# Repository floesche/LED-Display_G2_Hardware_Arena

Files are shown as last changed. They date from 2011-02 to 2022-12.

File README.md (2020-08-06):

---
title: Arena PCBs
parent: Generation 2
---

## Project content

```
├── arena_12_20
│   ├── gerber_v1
│   ├── gerber_v2
│   ├── pdf
│   └── svg
├── arena_12_20_top
│   └── gerber_v1
├── arena_mini
│   ├── gerber_v1
│   └── pdf
├── full
│   ├── 12-ring
│   └── 24-ring
├── mod
├── pdfs
├── planar_arena_8x
│   └── gerber_v0p1
└── planar_arena_8x_base
    ├── v0p1
    └── v0p2
```

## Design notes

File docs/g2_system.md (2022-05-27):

---
title: Generation 2
has_children: true
has_toc: false
nav_order: 20
permalink: /G2/
---

# Panels System

For a long time and since [Michael Reiser](https://www.janelia.org/people/michael-reiser) started an online documentation of the Modular LED Displays more than a decade ago, this introductory text had emphasized the community aspect of this endeavor. It is no small feat to design and produce electrical systems with high temporal and spatial precision that work reliably in many different scientific settings. Many labs have taken this task upon themselves and are building and using these systems. By now, the [Generation 2](g2_system.md) and [3]({{site.baseurl}}/G3/) Modular LED Displays have a large user basis across many scientific labs. We are also confident that the additional capabilities of the [Generation 4]({{site.baseurl}}/G4/) system will further the spread of this new stimulus presentation systems, especially once we had the chance to explain the advantages in the upcoming methods paper. Through all this, the exchange of experiences coupled with suggestions and improvements has benefited the system. Please [keep sending]({{site.baseurl}}/Contact) updates, improvements, and troubleshooting suggestions -- this is invaluable support for us in making the current and future systems better, but also for any future scientist who wants to replicate one of the systems in their setup.

To get started with [Generation 2](g2_system.md) or even a [Generation 3]({{site.baseurl}}/G3/) system, please have a look at this current page where we show some technical details of the system. A more general [user guide](g2_user-guide.md), written by Mark Frye, Michael Dickinson, and Michael Reiser, gives a nice and informal introduction to this system and its use as a flight arena for flies. Finally, we still consider the dated but [timeless paper](https://doi.org/10.1016/j.jneumeth.2007.07.019) that introduced the Modular LED Display back in 2007 a useful reference.

__Note__: For historical reasons we provide some information on how to [install](g2_prerequisites.md) a Generation 2 system, although we would strongly discourage anyone from doing this at this point. Follow the documentation of [Generation 4]({{site.baseurl}}/G4/) system instead or, if you want to use a less expensive system, have a look at the [Generation 3]({{site.baseurl}}/G3/) Modular LED Display instead.
{:.info}

# System Overview

The system has been designed to allow for rapid development of behavioral (visual) stimuli. There are three components to the system:

- __The displays__: These are 8×8 dot matrix displays of LEDs (either ready-made components or custom made [__LED matrices__]({{site.baseurl}}/Generation%202/LED-Arrays/docs/)) with the [__panel__]({{site.baseurl}}/Generation%202/Panels/docs/) electronics to turn individual LEDs on and off.
- __The controller__: a custom designed microprocessor circuit that communicates with a PC via the serial port and to the panels using a rapid serial interface (TWI). Note that TWI is Atmel's name for their own implementation of the I2C bus, a standard developed by Phillips.
- __PC software__: written in MATLAB, there are tools for generating patterns and sending commands to the controller.

In all the documentation that follows, we will try to use this terminology consistently:

- __The system__: refers to all of the components: displays, panels, controller, etc.
- __Setup__: refers to your particular configuration. This is mostly used in the context of the particular way in which you have the panels connected to the controller.
- __The Controller__: refers to the controller circuit board that is described in Section controller. This can be somewhat confusing, because the panels and controller boards both have microcontrollers on them, which both act as controllers. Furthermore, the MATLAB program is also controlling the controller. However, *the controller* will always refer to the controller circuit.
- __A Panel__: - refers to the module that is composed of both the circuit board and the LED display.
- __PControl__: - is the name of the MATLAB gui.

# TODO & Wish List

__Note__: This is the initial wish list published in 2006 with some additional comments on the status.
{:.info}

As presented the system is fully functional and has been in regular use for more than two years. However, there are many features that will improve the system. Here is a list of suggested projects. Some of these will be completed by the time you read this, (many will certainly not be). If anyone is interested in tackling these or suggesting other projects, please get in [contact]({{site.baseurl}}/Contact).

- programming of the panels from the MATLAB GUI, maybe even address them during programming. This would be done using the command line interface to the AVR Studio, or similar. *Possible but not yet implemented in Generation 3*
- A small box that converts ±5 V to two distinct 0-5 V lines, mapping positive voltage to one and negative to the other. This would really simplify using certain signals with controller. Ideally, put 2 of these in one box (will need independent power). __Not necessary with Generation 3, since inputs and outputs can go ±5 V.__
- program panels when they are plugged in, so they don't need to be programmed independently. Apparently this is possible, especially since the panels are set up to communicate with the TWI interface. Look at __Boot Loader Support__ section in the AVR documentation. __Generation 3 and more recent software development supports this.__
- re-mapable greenscales – the idea here is to be able to use binary, 2 level, patters and then be able to arbitrarily map the 0 and 1 values to any of the 8 greenscale levels. This scheme has basically been worked out (is in the distributed panels code, but commented out). This system needs to be tested, etc.
- more efficient CF reading – that would start moving the bytes from the FIFO before the pattern is completely dumped – this should provide at least 10% faster frame rates. __Superseded by faster SD card reading in Generation 3__
- more user-friendly installation that checks the CF card location, makes a temp folder if necessary, etc.
- Some buttons on the PControl GUI for quickly linking to experiment scripts.
- Move storage of internal function generator functions onto the CF card, maybe increase the temporal resolution (100 Hz seems reasonable), and allow the function buffer length to vary. __Implemented in Generation 3__

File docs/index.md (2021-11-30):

---
title: Arena
parent: Generation 2
nav_order: 6
---

# Arena boards

An arena board organizes panels in a geometry and provides structural integrity to the whole setup. Different shapes of cylindrical arenas have been built. We use a naming scheme based on their number of panel columns available and the virtual ones forming a full circle. A 12-12 arena is a closed cylinder formed by 12 columns in total, a 12-20 describes an open virtual cylinder formed by 20 columns where 12 are actually available. For planar or linear arenas the theoretical number of virtual columns is infinite, so an 8-inf arena describes a system with 8 columns in a row.

# Arena 12-12

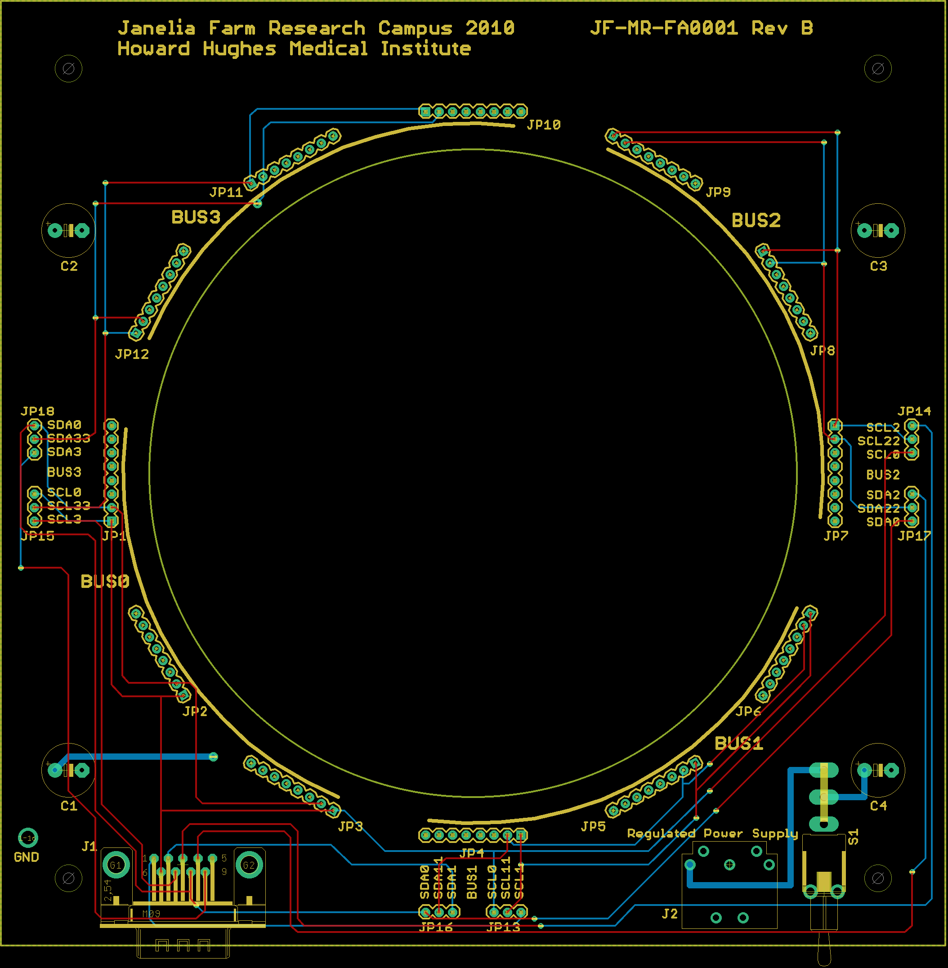
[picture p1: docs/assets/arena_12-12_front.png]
Front side of the Arena 12-12


The Arena 12-12 is an arena board for the Generation 2 of the Modular LED Display system. The original project file was named __JF-MR-FA0001__, the production files represent the __RevB__.

Find the EAGLE PCB for a 12-12 arena inside the `arena_12-12` project folder. Have a preview of the [schematic](assets/arena_12-12_schematic.pdf) or the [PCB layout](assets/arena_12-12_pcb.pdf). This arena was probably designed and produced around 2010.

# Arena 24-24

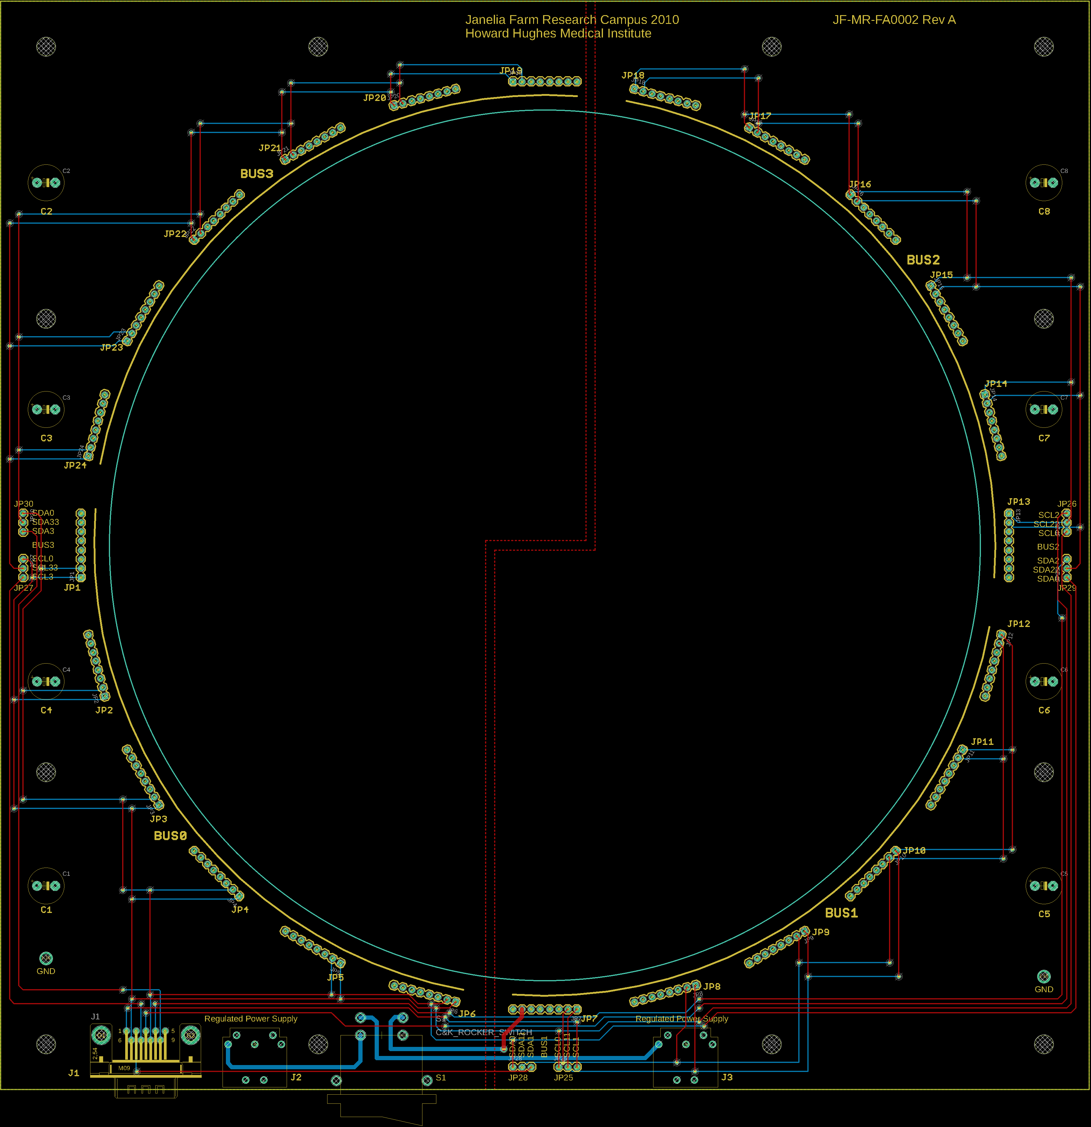
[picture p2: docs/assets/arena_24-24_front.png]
Front side of the Arena 24-24


The Arena 24-24 is an arena board for the Generation 2 of the Modular LED Display system. The original project file was named __JF-MR-FA0002__, the production files represent the __RevA__.

Find the EAGLE PCB for a 24-24 arena inside the `arena_24-24` project folder. Have a preview of the [schematic](assets/arena_24-24_schematic.pdf) or the [PCB layout](assets/arena_24-24_pcb.pdf). This arena was probably designed and produced around 2010.

# Arena 12-20

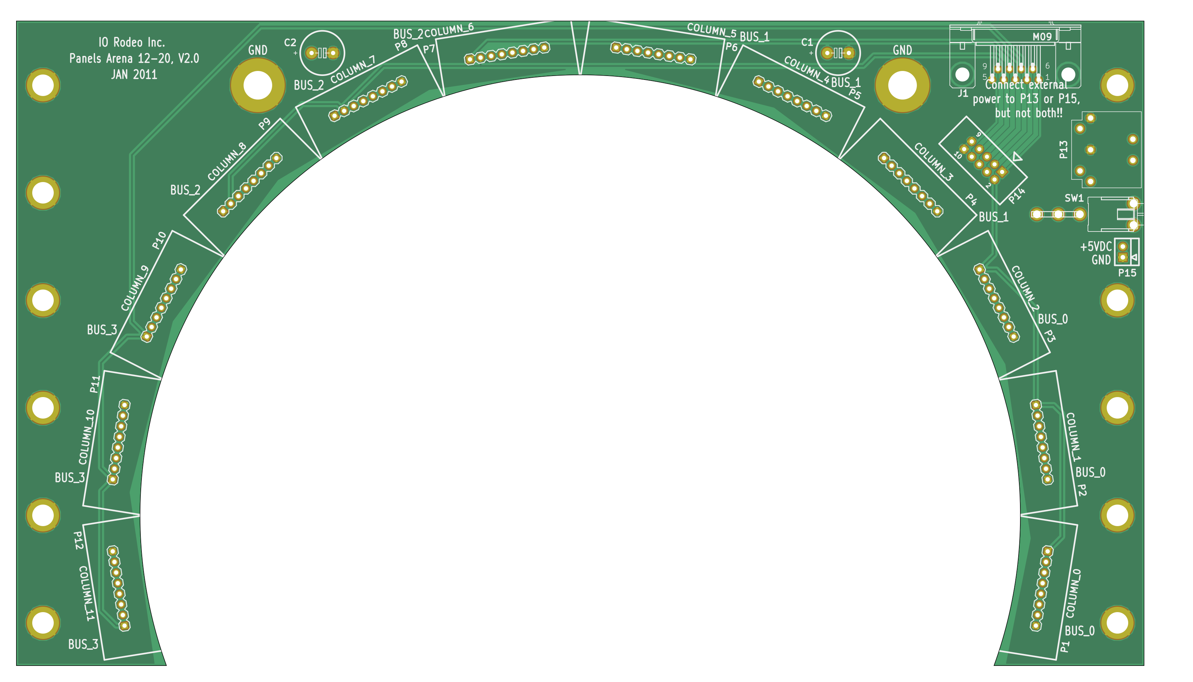
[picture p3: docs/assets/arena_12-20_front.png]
Front side of the Arena 12-20

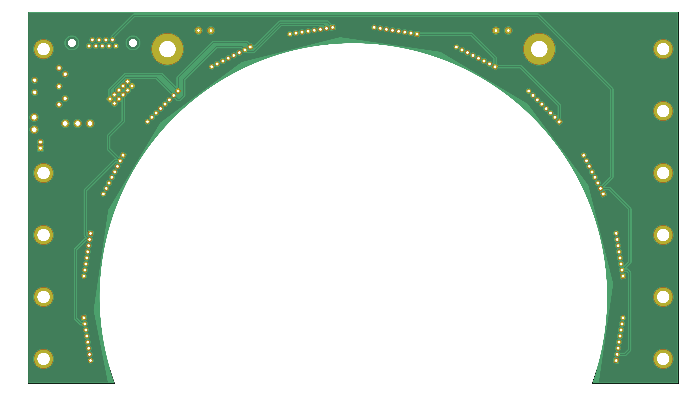
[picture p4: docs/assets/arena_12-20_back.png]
Back side of the Arena 12-20


The Arena 12-20 is an arena board for the Generation 2 of the Modular LED Display system. This is the board all panels are connected to.

Find the KiCad PCB for a 12-20 arena inside the `arena_12-20` project folder. Have a preview of the [schematic](assets/arena_12-20_schematic.pdf) or the [PCB layout](assets/arena_12-20_pcb.pdf).

This PCB was last ordered around 2011 from <https://protoexpress.com> under the name *panels_arena_12-20 2.0* reference number *192373-IRW* for about $75. Most likely, the content of `arena_12-20/production_v2/arena_12-20_v2p1.zip` was used for this order.

# Arena 12-20 TOP

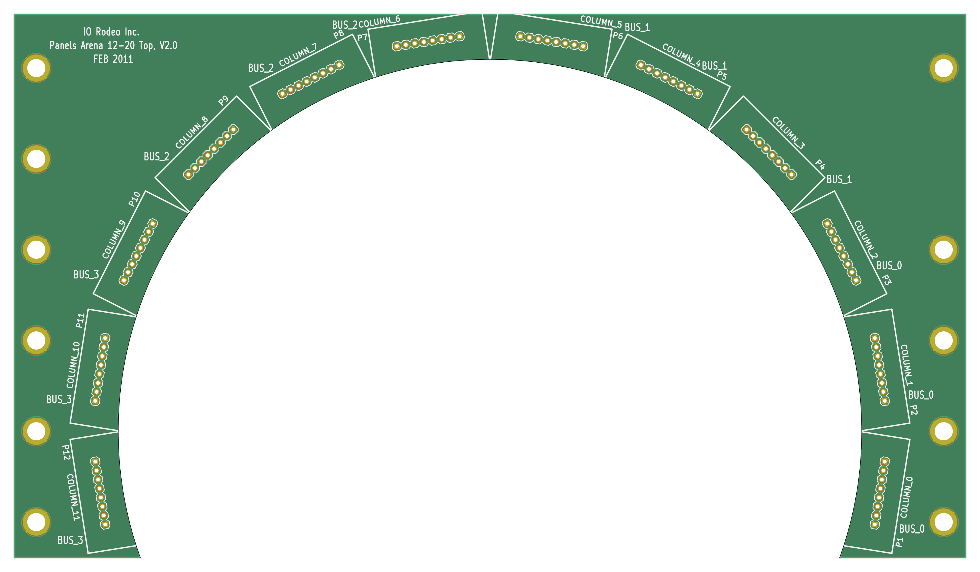
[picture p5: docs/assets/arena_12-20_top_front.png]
Front side of the Arena 12-20 TOP

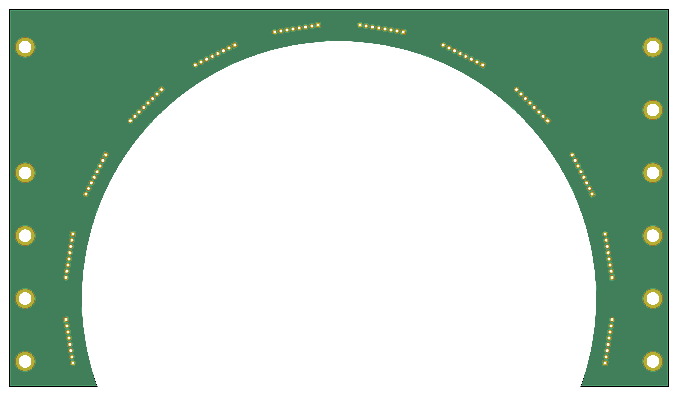
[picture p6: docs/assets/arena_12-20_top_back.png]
Back side of the Arena 12-20 TOP


The Arena 12-20 TOP board for the Generation 2 of the Modular LED DIsplay system is only used for mechanical stability. Except for the grounds, there are no other electrical connections between components.

Find the KiCad PCB for a 12-20 arena inside the `arena_12-20_top` project folder. Have a preview of the [schematic](assets/arena_12-20_top_schematic.pdf).

This PCB was last ordered around 2011 from <https://protoexpress.com> under the name *panels_arena_12-20_top 2.0* reference number *192373-IRW* for about $75. Most likely, the content of `arena_12-20_top/production_v1/arena_12-20_top_v1p0.zip` was used for this order.

# Arena 1-1

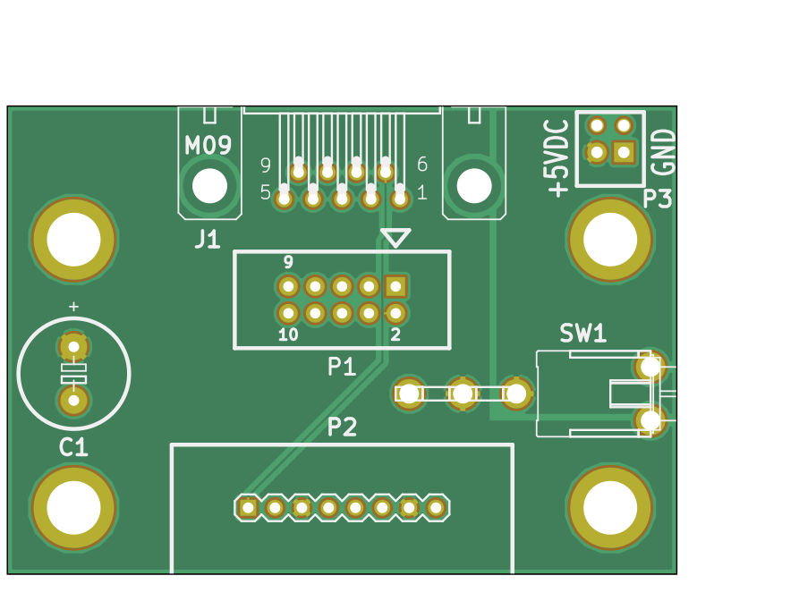
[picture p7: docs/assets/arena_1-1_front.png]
Front side of the Arena 1-1

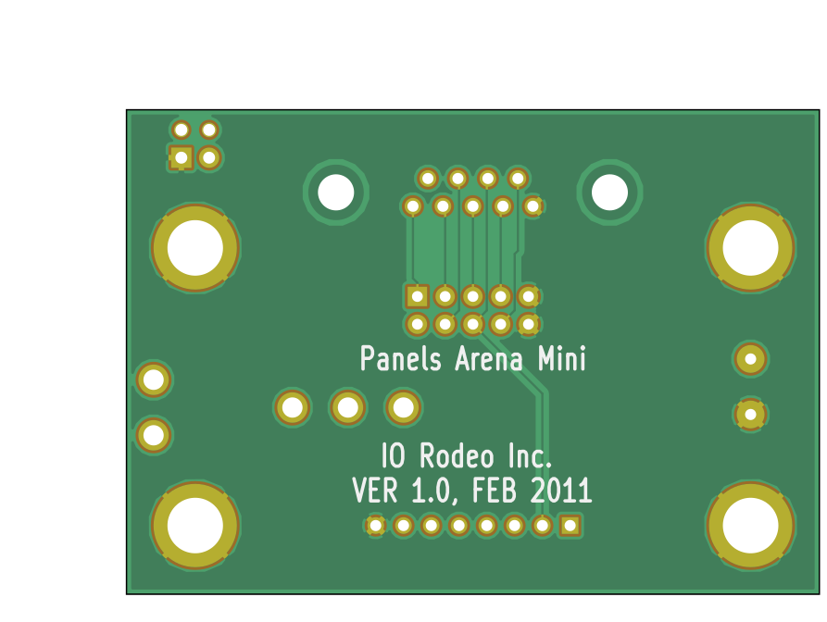
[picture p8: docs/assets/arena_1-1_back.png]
Back side of the Arena 1-1


The Arena 1-1 is a single panel arena board for the Generation 2 of the Modular LED Display system. It's primary use is development and debugging.

Find the KiCad PCB for a 1-1 arena inside the `arena_1-1` project folder. Have a preview of the [schematic](assets/arena_1-1_schematic.pdf).

This PCB was last ordered around 2011 from <https://protoexpress.com> under the name *panels_arena_mini 1.0 1.0* reference number *192719-INTJ* for about $2. Most likely, the content of `arena_1-1/production_v1/arena_1-1_v1p0.zip` was used for this order.

# Arena 8-inf

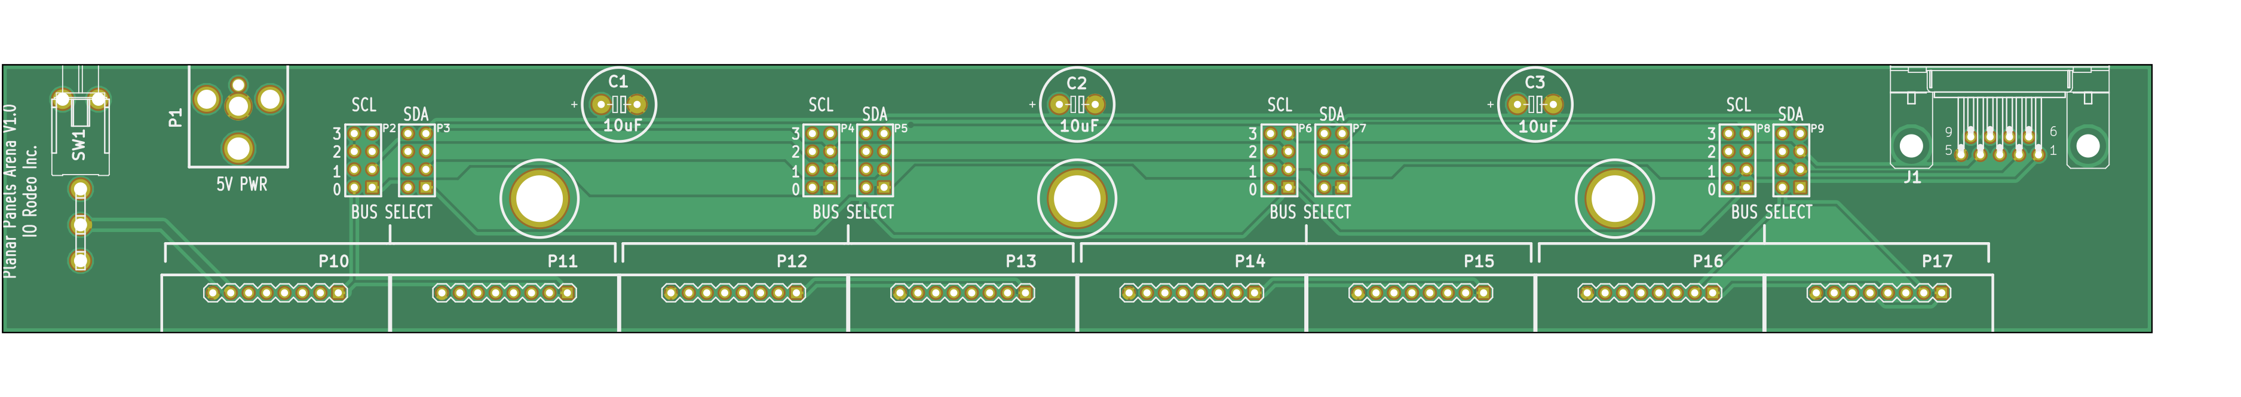
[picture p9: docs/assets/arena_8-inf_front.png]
Front side of the Arena 8-inf

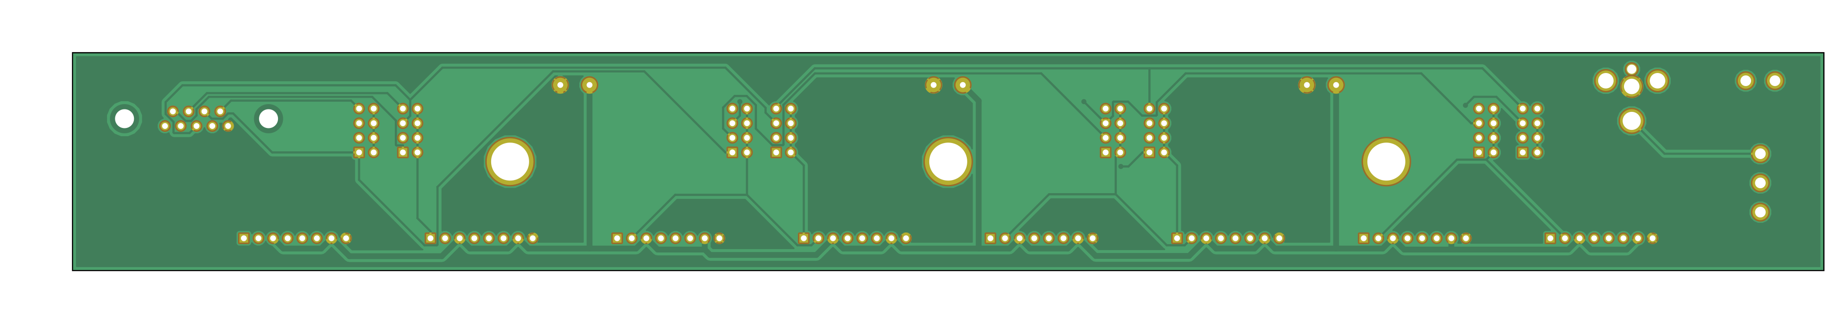
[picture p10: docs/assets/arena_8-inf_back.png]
Back side of the Arena 8-inf


The Arena 8-inf is a planar arena board with 8 panel connectors for the Generation 2 of the Modular LED Display system. It is sometimes referred to as a hallway arena.

Find the KiCad PCB for a 8-inf arena inside the `arena_8-inf` project folder. Have a preview of the [schematic](assets/arena_8-inf_schematic.pdf). In addition the project folder contains a folder named `enclosure`. These files were apparently used to produce some kind of mounting base or enclosure for the 8-inf arena. Based on the vector file format the parts were probably laser cut. There is also a python file to generate a OpenSCAD file.

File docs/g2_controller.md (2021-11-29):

---
title: Controller
parent: Generation 2
nav_order: 3
---

# Controller

The Controller reads in pattern data from the CF card memory, accepts commands from the PC control program, and sends pattern data to the panels over the TWI bus.

## Controller Hardware {#hardware}

The controller board contains 2 ATmega128 micro controller units (MCU), one is dedicated to reading the pattern data from the CompactFlash card, and the other communicates with the PC and the panels display. The PCB design has been modified, so that connections with a case are rather simple.

- [Controller v2.2 PCB (pdf)](assets/controller_pcb_v2p2.pdf)
- [Controller v2.2 schematic (pdf)](assets/controller_schematic_v2p2.pdf)

## Power supplies

There are 2 options for supplying power to the controller board. An unregulated supply can be connected to the 3-pin header. This power is regulated down to 5 volts and used by the circuitry on the board. An inexpensive DC wall transformer is a good choice, at least 9V and 1-2 A, should be adequate. Use this connector when no panels (or just 1 or 2) are on the controller. The three pins are [`GND` `V+` `GND`], the suggested connector to use is a three pin female: [`GND` `V+` `Blank`]. This way there is no possibility of switching power and ground. The other option is a 5-Pin DIN connector regulated supply. Looking head on at the supply connector, should have (Left to Right): Ground, no connect, Ground, no connect, + 5V. The two pins are not connected, so if a pre-built supply has something on these pins, it will be fine to use this supply, otherwise, modify the connector to this pin-out. The 5V, 10A power supply given in the [parts list](#parts-list) works very well.

## Controller Software

The software running on the Controller is essentially the intermediary between the commands sent from the PControl program detailed in section…, and the panels. The following section explains how and what the code does, read this if you are curious or plan on modifying the code. Hopefully most users can use the system directly from MATLAB and remain blissfully ignorant of these details. The software on the controller has been designed with one goal - making sure patterns are streamed to the panels as quickly as possible, keep this in mind if some of this seems peculiar.

### Programming the Controller

Programming the controller is similar to the process for programming each panel. There is a 6-pin ISP interface for both of the controller board's ATmega128 microprocessors. Let's program the main controller first:

1. Power the Controller board if using the AVR ISP, otherwise power the STK 500, and connect the programming device to the 6 pin Controller ISP header (labeled J7 on the PCB).
2. Open AVR Studio and start the AVR programming tool STK500/AVRISP from the tools menu.
3. Test the connection by selecting the ATmega128 device from the drop-down menu, and then in the advanced tab try to read signature. If these match, move on, otherwise check the connections (rotate connector), restart, etc.
4. Program the fuses - this is done from the __Fuses__ tab - a few options should be set: __ATMega103 compatibility mode__ must be set to OFF, __JTAG interface enable__ must be set to OFF, and clock rate must be set to the last choice: __Ext. Crystal/Resonator High Freq.: Start-up time 16K CK + 64 ms__. It is also a good idea to set __Brown-out detection level at VCC=4.0V__ and __Brown-out detection enabled__.
5. There is no EEPROM file needed for this application.
6. Program the flash on the ATmega128 by selecting the __Program__ tab and selecting the input hex file as: `mainctrl.hex`, and then programming the chip.
7. It is always a good idea to verify both the program and the fuses to make sure these are set correctly.
8. To program the CompactFlash controller, just repeat steps 1-7, except for:
    1. Unplug the CF card if there is one in the socket. Also plug the 6 pin ISP cable into the 6 pin ISP header for the CF controller (labeled J8 on the PCB).
9. program with the file `cfctrl.hex`.

# Parts list {#parts-list}

These parts are required to make 1 controller (compiled around 2006):

| quantity | part description               | source & p/n | price |
|---------:|:-------------------------------|:------------ |------:|
| 2        | [ATmega128](http://www.atmel.com/dyn/resources/prod_documents/doc2467.pdf) microcontroller, 64 TQFP package | Digi-Key, ATMEGA128-16AI-ND | $10 |
| 1        | [CY7C4251V-15AC FIFO](https://datasheet.octopart.com/CY7C4251V-15AC-Cypress-Semiconductor-datasheet-13109.pdf), 32 TQFP package | Digi-Key, 428-1229-ND | $18 |
| 2        | [DAC 8571](http://focus.ti.com/lit/ds/symlink/dac8571.pdf), I2C 16 bit, 8 MSOP package | Digi-Key, 296-14307-1-ND | $5 |
| 1        | [Maxim RS-232 driver](https://datasheet.octopart.com/MAX233ACPP-Maxim-datasheet-3759.pdf) | Digi-Key, MAX233ACPP-ND | $8 |
| 5        | 150Ohm 1/4W resistor, 1206 package | Digi-Key, 311-150ECT-ND | $0.02 |
| 9        | 10kOhm 1/4W resistor, 1206 package | Digi-Key, 311-10KECT-ND | $0.02 |
| 2        | 16 MHz crystal oscillator          | Digi-Key, X192-ND | $0.70 |
| 1        | BNC connector, vertical PCB, mount | Digi-Key, A24504-ND | $1.50 |
| 1        | CF connector                       | Digi-Key, 478-2012-ND | $3.00 |
| 2        | 10-pin ribbon connector            | Digi-Key, M3AAA-1006R-ND | $2.50 |
| 2        | 6-pin male double-row headers      | Digi-Key, | |
| 1        | 7805T, 5 V regulator (optional)    | Jameco, 51262 | $0.30 |
| 1        | 10uH RF choke (inductor)           | Jameco, 208135 | $0.60 |
| 1        | 10µF capacitors, tantalum          | Jameco, 33689 | $0.60 |
| 8        | 0.1µF coupling caps, tant.         | Jameco, 332110 | $0.20 |
| 2        | 20-pin DIP socket                  | Jameco, 38607CL | $0.10 |
| 5        | rt. Angle, PCB mount LEDs          | Jameco, 104256(gr.), 104248(red) | $0.25 |
| 2        | push button switches               | Jameco | |
| 4        | 22pF (20%) capacitors              | Jameco, 15405 | $0.05 |
| 3        | 9 pin fem. rt. angle D-sub         | Jameco, 104951 | $0.50 |
| 1        | 5 pin fem. DIN connector           | Jameco, 29399 | $0.50 |
| 12       | male single row 0.1" header        | Jameco, 160881 | $0.40 |
| 4        | fem. single row header, 8 pin      | Jameco, 70754 | $0.40 |
| 2        | TWI resistors – std. 1k Ohm        | Jameco, 29663 | peanuts |
| 1        | SPST toggle switch                 | Jameco, 76523 | $1.00 |
| 1        | power supply, 5V, min. 2A          | Jameco, 221487 (w DIN conn.) | $35 |
| 1        | Controller PCB                     | ordered from Advanced Circuits | |

__Notes__: male single row headers are needed in sizes of 2 and 3 - easiest thing to do is cut these from a larger strip. Female single row headers are needed in 8 row size, so easiest thing is to order these as a pre-sized piece from Jameco (also needed for flight arenas).

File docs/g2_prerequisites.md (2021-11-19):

---
title: Prerequisites
parent: Generation 2
nav_order: 2
---

# Installation and Prerequisites

There are some basic tools needed to use the system:

- A PC running a recent version of Windows. The PC must have at least 1 serial port, although 2 (or even 3) would be useful. To easily add serial ports to your computer, consider a USB to Serial converter. [Here are some](http://www.usbgear.com/USB-Serial.html).
- [MATLAB](https://www.mathworks.com ) installed on this PC - the code should work on all MATLAB releases, but is currently only tested on releases from 2009 onwards.
- A Programming device for the Atmel microcontrollers. Either the [AVR ISP mkII](http://www.atmel.com/dyn/products/tools_card.asp?tool_id=3808&category_id=163&family_id=607&subfamily_id=760) or the [AVR STK500](http://www.atmel.com/dyn/products/tools_card.asp?tool_id=2735). The AVR ISP [Digi-Key p/n ATAVRISP2-ND](https://www.digikey.com/products/en?keywords=ATAVRISP2-ND) is a stand alone programmer that connects to a PC via USB on one end, and has the 6 pin programming interface which is used to program the controller and the panels. The [AVR STK500](https://www.digikey.com/short/z9zd3h) has the programming interface, but is also a starter kit and development system for Atmel microcontrollers.
- AVR studio or other set of AVR tools - this is useful if you plan to make any modifications to the software running on either the controller or the panels. The AVR studio has a nice GUI for programming Atmel microcontrollers through either the AVR ISP or AVR STK500. More information at www.atmel.com and www.avrfreaks.net.
- Power supplies - see [Controller Hardware](g2_controller.md#hardware) for details.
- Compact Flash (CF) card and reader. Any USB-based CF (or multi-format) reader will work. Even large patterns only require space measured in kilobytes, so any available CF card will be large enough, but it is advisable to get a high speed card. The fastest card we measured was a 128 MB Dane-Elec 45X card.
- Many experiments can be made simpler by generating signals from MATLAB that can be used to encode some information about the current trial (this signal is then acquired along with any other experimental data). An inexpensive and reliable product for doing this is one of the USB DAQ modules from <http://www.mccdaq.com/>. We have been using the 1208 series that has 2 analog output signals and is supported by the MATLAB DAQ toolbox.

__Note__: currently the system seems not to work with cards that are larger than 128 MB. This is certainly a solvable problem, but buying 128 MB cards is the best option currently. These cards are increasingly harder to find, one reason that PDC v3 uses SD cards. One vendor that still carries these is <http://www.flash-memory-store.com/>.
{:.info}

# Download Code & PCB files

This code is no longer officially supported or maintained, but has been used for years by at least 10 labs. The code is distributed _as is_; it works for me and I hope it works for you. __Michael Reiser and the Dickinson Lab are not liable for any damage caused by using (or misusing) this code.__ Remember, programming microcontrollers is not as safe as PC programming, extreme caution must be taken to ensure that all connections are correct, and that the circuit boards are functioning – if anything smells like it is burning or gets hot – turn off immediately and recheck everything.

- [Panel Files Release 2](assets/panels_r2.zip)

There are many changes that are included in the second release:

- New control modes, numeric position control. This uses the function generator to numerically specify the current position. Implemented as a (signed) offset to the position specified by `Panel_com('set_position', [X,Y])`.
- System can now support much larger patterns – previously a frame was limited to one block of the CF memory – 512 bytes. Now multi-block frames are supported. Tested with 48 display gscale patterns (1152 bytes per frame).
- CF reading is slightly faster, no longer reads entire block, but stops once the number of bytes in the frame have been read.
- Row compression: for patterns that consist of identical data for all rows of the pattern. RC is enabled by setting pattern.row_compression = 1; in  the pattern-making script. An RC pattern will just consist of one row instead of 8, resulting is a speedup factor of at least 5. This feature required modification to the code on the main and CF controllers, the panel code, and a few of the MATLAB pattern making and displaying routines.
- Identity compression: For patterns that contain large swaths of pixels that are simply on or off. The controller can check to see if this is the case, and then just send the row-compressed version of the display data for a display that corresponds to a pattern piece that is all one value (works for grayscale too!). This feature is not used at pattern making time, but rather while the pattern is running. Identity compression can be enabled by invoking: `Panel_com('ident_compress_on')` from MATLAB.
- New (simpler) serial port interface from MATLAB. Fixes previous problem sending certain values (byte values above 127) over the serial port.
- Two new digital outputs: pulse to trigger a laser depending on pattern position, and an adjustable clock signal to trigger a camera. These are supported by commands in the `panel_com` function.
- Most of the C code (controller programs and the G3 panel code) is now compatible with newest version of GCC compiler. This required including a legacy.h file.
- Now releasing code for 3 generations of panels. The code in the previous release is now considered Generation 2 (G2) code. Generation 3 (G3) code is only slightly modified from Generation 2 to support a new chip – the ATmega168 (slightly faster, bigger flash), using the same panel PCB. Generation 1 code is included for the convenience of Dickinson Lab members who are still using the original design. All controller code is compatible with all 3 generations of panels.
- The distribution includes PCB files for a 12 display ring, the typical configuration of a flight arena.

All files are being distributed in a single .zip file. This file contains 3 folders:

- `c code` - code for the panels and the controller board. Each subfolder also contains the .hex file needed to program the individual microcontrollers. If no modification will be made to the c code, then the compiled .hex files are sufficient to build the system. To edit and compile the AVR c code, you will need to install a GCC compiler for the Atmel AVRs. We recommend the [WinAVR](http://winavr.sourceforge.net/ ) package, but there are others out there. Some of the modules used in the AVR c code, are taken from the Procyon AVRlib (link broken) package written by Pascal Stang. The code from the AVRlib is included in the distributed .zip file above, so you will not need to download this package, but you are encouraged to do so if you plan to do any serious Atmel programming.
- `schematics` – schematic and PCB files for the panels and the controller. These files were created in Protel 99 SE. Each folder also contains a subfolder with all of the CAD files that are needed to order the PCBs.
- `MATLAB panels code` – contains a folder called `matlabroot` that contains a series of subfolders. To set this up on a new system, the folder should be copied to the `C:\` drive (you want the subfolders to reside under `C:\matlabroot`). It is important to add these new folders and all subfolders to the MATLAB path. There is a file called `panel_control_paths.m` that should be updated with the appropriate paths for the specified files, so that the installation will function on your PC. You will also need to the file [dd.exe](http://www.chrysocome.net/dd) (*Note: the original documentation linked to <http://uranus.it.swin.edu.au/~jn/linux/rawwrite/dd-0.3.zip> which is broken. The file is included in the zip, but should you require a different version, the above link might help you to get started*), but this is included in the folder of other files. This file is necessary to burn images onto the CompactFlash cards (from Windows). In `matlabroot\Panels\IO_tools\` there is a file called `get_CF_drive.m`, this file contains a hard-coded drive letter for the CF drive - you should update this letter to reflect your system.

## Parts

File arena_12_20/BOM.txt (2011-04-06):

-*- mode:org -*-

# panels_ring_12_20.lst
| ref | value      |
|-----+------------|
| C1  | CAPAPOL    |
| C2  | CAPAPOL    |
| J1  | DB9        |
| P1  | COLUMN_0   |
| P2  | COLUMN_1   |
| P3  | COLUMN_2   |
| P4  | COLUMN_3   |
| P5  | COLUMN_4   |
| P6  | COLUMN_5   |
| P7  | COLUMN_6   |
| P8  | COLUMN_7   |
| P9  | COLUMN_8   |
| P10 | COLUMN_9   |
| P11 | COLUMN_10  |
| P12 | COLUMN_11  |
| P13 | DIN_5      |
| P14 | CONN_5X2   |
| P15 | CONN_2     |
| P16 | CONN_1     |
| P17 | CONN_1     |
| P18 | CONN_1     |
| P19 | CONN_1     |
| P20 | CONN_1     |
| P21 | CONN_1     |
| P22 | CONN_1     |
| P23 | CONN_1     |
| P24 | CONN_1     |
| P25 | CONN_1     |
| P26 | CONN_1     |
| P27 | CONN_1     |
| P28 | CONN_1     |
| SW1 | SWITCH_INV |

# Bill of Materials
| ! | part   | description                      | vendor       | part number   | quantity |   cost |
|---+--------+----------------------------------+--------------+---------------+----------+--------|
|   | PCB    | panels_arena_12-20 2.0           | protoexpress | 192373-IRW    |        1 |  74.13 |
|   | C1-2   | CAP TANTALUM 10UF 25V 10% RAD    | digikey      | 478-4170-ND   |        2 |   0.81 |
|   | J1     | CONN D-SUB PLUG R/A 9POS GOLD/FL | digikey      | A35113-ND     |        1 |   1.91 |
|   | P1-12  | CONN RCPT .100" 8POS SNGL TIN    | digikey      | SAM1222-08-ND |       12 |   1.67 |
|   | P13    | CONN DIN 5 PIN FEMALE PCB        | digikey      | CP-2350-ND    |        1 |   1.20 |
|   | P14    | CONN HEADER 2.54MM 10POS GOLD    | digikey      | S9169-ND      |        1 |   0.31 |
|   | P15    | CONN TERM BLOCK 2.54MM 2POS      | digikey      | 277-1273-ND   |        1 |   1.10 |
|   | P16-28 | SCREW MACHINE PHIL 8-32X3/8 SS   | digikey      | H715-ND       |       13 |   0.12 |
|   | P16-28 | STANDOFF HEX 8-32THR ALUM .500"L | digikey      | 2217K-ND      |       13 |   0.45 |
|   | SW1    | SWITCH TOGGLE SPDT SEAL VERT R/A | digikey      | CKN1513-ND    |        1 |   6.93 |
|---+--------+----------------------------------+--------------+---------------+----------+--------|
| # | total  |                                  |              |               |          | 114.65 |
#+TBLFM: @12$7=(@I$quantity..@II$quantity)*(@I$cost..@II$cost);%.2f;N

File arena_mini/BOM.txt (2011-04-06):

-*- mode:org -*-

# panels_arena_mini.lst
| ref | value      |
|-----+------------|
| C1  | CAPAPOL    |
| J1  | DB9        |
| P1  | CONN_5X2   |
| P2  | COLUMN_0   |
| P3  | CONN_2     |
| P4  | CONN_1     |
| P5  | CONN_1     |
| P6  | CONN_1     |
| P7  | CONN_1     |
| SW1 | SWITCH_INV |

# Bill of Materials
| ! | part  | description                                               | vendor       | part number   | quantity |  cost |
|---+-------+-----------------------------------------------------------+--------------+---------------+----------+-------|
|   | PCB   | panels_arena_mini 1.0                                     | protoexpress | 192719-INTJ   |        1 | 21.56 |
|   | C1    | CAP TANTALUM 10UF 25V 10% RAD                             | digikey      | 478-4170-ND   |        1 |  0.81 |
|   | J1    | CONN D-SUB PLUG R/A 9POS GOLD/FL                          | digikey      | A35113-ND     |        1 |  1.91 |
|   | P1    | CONN HEADER 2.54MM 10POS GOLD                             | digikey      | S9169-ND      |        1 |  0.31 |
|   | P2    | CONN RCPT .100" 8POS SNGL TIN                             | digikey      | SAM1222-08-ND |        1 |  1.67 |
|   | P3    | CONN TERM BLOCK 2.54MM 2POS                               | digikey      | 277-1273-ND   |        1 |  1.10 |
|   | P4-7  | SCREW MACHINE PHIL 8-32X3/8 SS                            | digikey      | H715-ND       |        4 |  0.12 |
|   | P4-7  | STANDOFF HEX 8-32THR ALUM .500"L                          | digikey      | 2217K-ND      |        4 |  0.45 |
|   | SW1   | SWITCH TOGGLE SPDT SEAL VERT R/A                          | digikey      | CKN1513-ND    |        1 |  6.93 |
|   |       | IDC Female 10 Position 2.54mm IDT Right Angle Cable Mount | jameco       | 525309        |        2 |  1.19 |
|   |       | CABLE 10 COND 5' GRAY RIBBON                              | digikey      | AE10G-5-ND    |        1 |  1.44 |
|---+-------+-----------------------------------------------------------+--------------+---------------+----------+-------|
| # | total |                                                           |              |               |          | 40.39 |
#+TBLFM: @13$7=(@I$quantity..@II$quantity)*(@I$cost..@II$cost);%.2f;N

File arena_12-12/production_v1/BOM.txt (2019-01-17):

===============
Bottom Assembly
===============

part      description                               vendor      part#         qty    
---------------------------------------------------------------------------------------
J1         CONN D-SUB PLUG R/A 9POS GOLD/FL         digikey     609-1478-ND    1    
J2         CONN DIN 5 PIN FEMALE PCB                digikey     CP-2350-ND     2    
S1         SWITCH,TOG,SPDT,ON-ON(M148PC)            digikey     CKN-1513-ND    1     
JP1-JP12   CONN RCPT .100" 8POS SNGL TIN            digikey     SAM122-08-ND   24   
C1-C4      CAP TANTALUM 10UF 25V 10% RAD            digikey     478-4170-ND    4     
JP13-JP18  CONN HEADER 3POS .100" STR TIN           digikey     WM8073-ND      6     
 
============
Top Assembly
============

part      description                               vendor      part#         qty    
---------------------------------------------------------------------------------------
JP1-JP12  HEADER,.1 ST MALE,1RW,8PIN, .025 PST,.23  digikey    S1011EC-40-ND  24

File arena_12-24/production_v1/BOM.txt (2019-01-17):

===============
Bottom Assembly 
===============

part      description                               vendor      part#         qty   
------------------------------------------------------------------------------------
J1         CONN D-SUB PLUG R/A 9POS GOLD/FL         digikey     609-1478-ND    1    
J2,J3      CONN DIN 5 PIN FEMALE PCB                digikey     CP-2350-ND     2    
S1         Power switch, rocker                     digikey     CKN10017-ND    1
JP1-JP24   CONN RCPT .100" 8POS SNGL TIN            digikey     SAM122-08-ND   24   
C1-C8      CAP TANTALUM 10UF 25V 10% RAD            digikey     478-4170-ND    8    
JP25-JP30  CONN HEADER 3POS .100" STR TIN           digikey     WM8073-ND      6    

============
Top Assembly
============

part      description                               vendor      part#         qty   
------------------------------------------------------------------------------------
JP25-JP24  HEADER,.1 ST MALE,1RW,8PIN, .025 PST,.23  digikey    S1011EC-40-ND  24

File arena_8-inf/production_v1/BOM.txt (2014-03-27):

Description                                    Vendor        PN             Price      Qty
-------------------------------------------------------------------------------------------
CAP TANT 10UF 25V 10% RADIAL                   Digikey      478-4170-ND      $0.81      2
CONN D-SUB PLUG R/A 9POS GOLD/FL               Digikey      A35113-ND        $2.00      2 
CONN HEADER 2.54MM 10POS GOLD                  Digikey      S9169-ND         $0.31      2
CONN HEADER 4POS .100 STR TIN                  Digikey      609-3242-ND      $0.32      2
CONN PWR JACK DC 2.1X5.5 8A T/H                Digikey      CP-063AH-ND      $1.55      2
CONN RCPT .100" 8POS SNGL TIN                  Digikey      SAM1195-08-ND    $1.62      7
SWITCH TOGGLE SPDT SEAL VERT R/A               Digikey      CKN1513-ND       $7.14      2

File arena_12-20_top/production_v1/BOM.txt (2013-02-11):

-*- mode:org -*-

# panels_ring_12_20_top.lst
| ref | value     |
|-----+-----------|
| P1  | COLUMN_0  |
| P2  | COLUMN_1  |
| P3  | COLUMN_2  |
| P4  | COLUMN_3  |
| P5  | COLUMN_4  |
| P6  | COLUMN_5  |
| P7  | COLUMN_6  |
| P8  | COLUMN_7  |
| P9  | COLUMN_8  |
| P10 | COLUMN_9  |
| P11 | COLUMN_10 |
| P12 | COLUMN_11 |
| P18 | CONN_1    |
| P19 | CONN_1    |
| P20 | CONN_1    |
| P21 | CONN_1    |
| P22 | CONN_1    |
| P23 | CONN_1    |
| P24 | CONN_1    |
| P25 | CONN_1    |
| P26 | CONN_1    |
| P27 | CONN_1    |
| P28 | CONN_1    |

# Bill of Materials
| ! | part   | description                    | vendor       | part number   | quantity |   cost |
|---+--------+--------------------------------+--------------+---------------+----------+--------|
|   | PCB    | panels_arena_12-20_top 2.0     | protoexpress | 192373-IRW    |        1 |  74.13 |
|   | P1-12  | CONN HEADER 8POS .100 PCB GOLD | digikey      | SAM1043-50-ND |        2 |   3.76 |
|   | P18-28 |                                |              |               |       11 |   0.00 |
|---+--------+--------------------------------+--------------+---------------+----------+--------|
| # | total  |                                |              |               |          |  81.65 |
#+TBLFM: @5$7=(@I$quantity..@II$quantity)*(@I$cost..@II$cost);%.2f;N

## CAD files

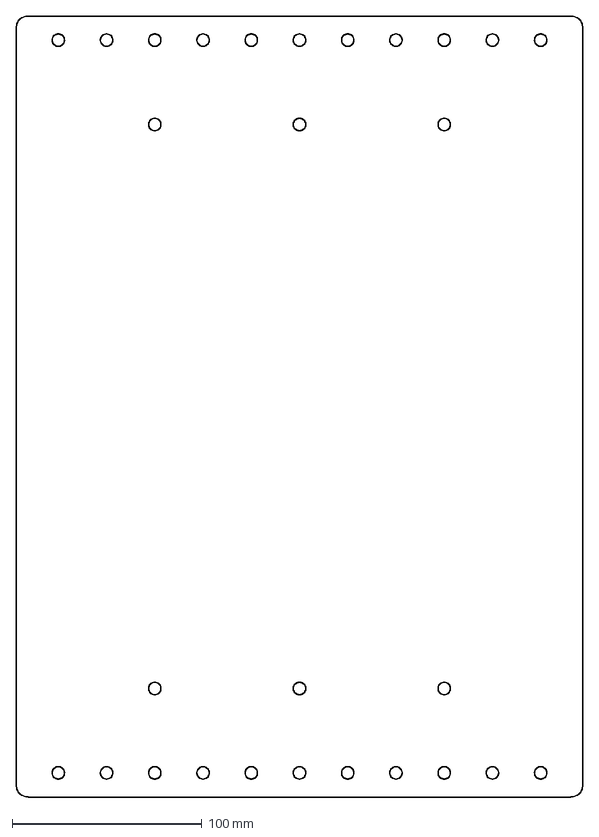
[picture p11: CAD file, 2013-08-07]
arena_8-inf/enclosure/v0p1/planar_arena_8x_base.dxf
298.4 x 411.3 mm

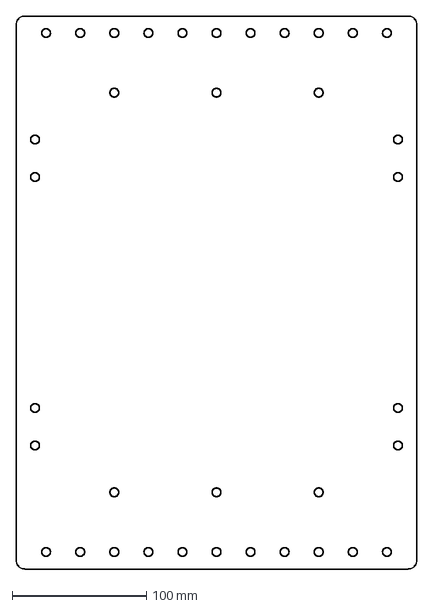
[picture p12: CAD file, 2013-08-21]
arena_8-inf/enclosure/v0p2/base.dxf
298.4 x 412.2 mm

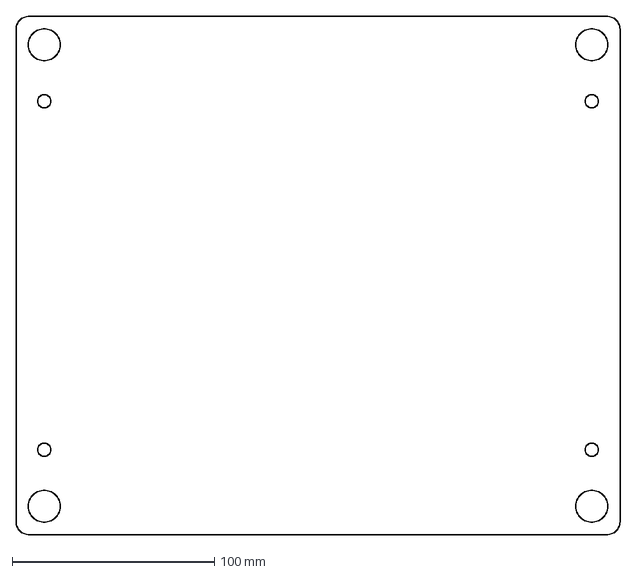
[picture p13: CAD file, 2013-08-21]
arena_8-inf/enclosure/v0p2/lower.dxf
298.4 x 256.0 mm

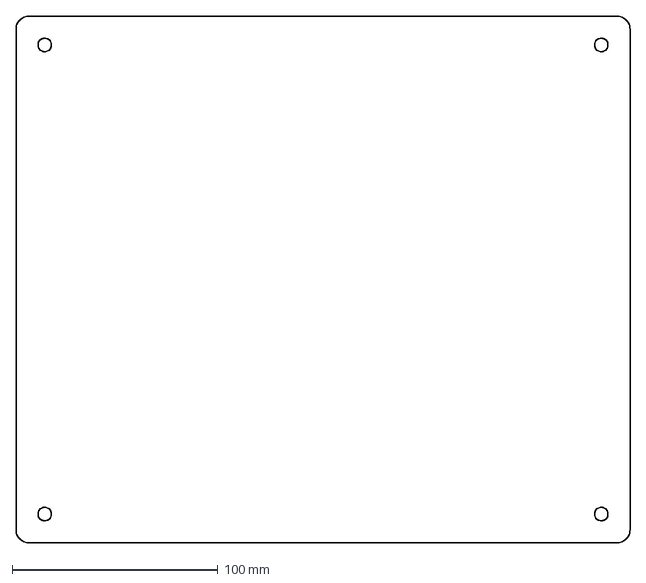
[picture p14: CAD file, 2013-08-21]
arena_8-inf/enclosure/v0p2/upper.dxf
298.4 x 256.0 mm

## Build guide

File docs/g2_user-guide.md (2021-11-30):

---
title: User Guide
parent: Generation 2
nav_order: 1
---

# Theory and Practice of Insect Flight Simulators

Authors: Mark Frye, Michael Reiser, Michael Dickinson

# History and principles of operation

The devices and techniques described in this document owe much to approaches developed at the Max Planck Institute for Biological Cybernetics in Tübingen, Germany.  This institute grew in the early 1960s around a group of four scientists: Werner Reichardt, Karl Götz, Valentino Braitenberg, and Kuno Kirschfeld, who adopted the visual system of flies as a general model system for neural processing. The term 'Biological Cybernetics' was used to describe to use of information theory, computer science, control theory, etc. to characterize biological systems- the term 'reverse engineering' is often used today to describe similar approaches. This enterprise generated a remarkable body of work, which ranged from detailed anatomical descriptions of visual system circuitry (e.g. discovery of 'neural superposition' in the fly) to sophisticated behavioral and physiological measurements (e.g. characterization of the lobula plate tangential cell system) to development of mathematical model of neural processing (e.g. refinement of the Hassenstein-Reichardt elementary movement detector model).

Perhaps less appreciated, was the work of Karl Götz, who developed an ingenious set of experimental methods for studying the optomotor control of flight in the fruit fly, *Drosophila melanogaster*. The work influenced not only the techniques described here, but also served as the direct foundation for many recent studies of visual spatial memory in *Drosophila*. The focus of his pioneering work was to produce visual stimuli with specific spatial and temporal properties, record the resultant behavioral responses, and then derive the intervening transfer functions. By formalizing the functional relationships between visual input and motor output, he was able to develop and test specific hypotheses about the underlying neural structures. The work was made enormously challenging because there was no "off the shelf" instrumentation at all for such experiments. Götz literally drew the plans for the devices he used throughout his career, often leaving them on the desk of the chief institute machinist before walking home in the early hours of the morning. Götz spent equal time developing ingenious ways of presenting visual stimuli to flies, and clever ways of recording, quantitatively, how the flies responded.  One early device was a complex braid of fiber optic filaments that took the images displayed on an analog oscilloscope and wrapped them into a cylinder surrounding the fly. Another device employed active electromechanical feedback to record the yaw torque generated by a tethered fly. One of his more ingenious experimental techniques was a system that optically tracked the beating wings of a tethered fly, and electronically coupled these signals to rotation of a spinning glass disk, such that light projected through fish eye optics created a pattern of stripes and spots on a circular cylinder surrounding the fly. As the fly (suspended in the middle of a rotating striped drum) tried to turn left, bilateral changes in wing stroke amplitude triggered servomotors to rotate the drum to the right. Under these conditions, the fly has "closed-loop" control over the visual panorama. Using such systems, Götz pioneered studies that linked the responses of the flies visual system to its motor responses in the form of muscle activity, wing motion, and aerodynamic forces.

Recent technical advances have made flight simulators easier to build and more sophisticated, but the basic architecture remains: present a visual stimulus to the fly, record what it does (in open loop), or provide it with the opportunity of changing what it sees (in closed loop). The new systems are modular and fully programmable for visual images of varying brightness, contrast, and spatial layout.

# Tethering Flies

The most critical step in collecting high quality data in a flight simulator is tethering the animals. Well-chosen, healthy, properly-tethered (i.e. 'happy') flies will generate hours of data each day. Crappy flies (*sensu* Reiser), poorly tethered are not worth putting in the arena. Here are a few hints regarding the choice and care of flies in preparation for tethering:

- It is quite helpful to use flies reared at low density in bottles, as opposed to high density in vials, as is unfortunately standard in genetics labs.
- Animals that are 2-3 days old generally provide the best data, but older flies will work if the are healthy.
- Females fly longer and more readily than males, but this may simply be a scaling effect – female flies are much larger and thus contain greater energy reserves. Large gravid females (with big white abdomens) seem to be the most behaviorally robust. A good, healthy 1.2 mg female will fly for about 1 hour, depending on the experiment.
- In most experiments, it is convenient to starve flies for 4-8 hours. Starved flies tend to fly more. When starving, provide a damp kimwipe in the vial or bottle so that the flies do not desiccate.
- Flies are crepuscular animals with activity peaks in the early morning and late afternoon – when it is cool enough to fly and light enough to see. Keep your flies on a strict light:dark cycle and perform your experiments during their crepuscular peaks. The afternoon peak is typically the most convenient. Woe to those that think such details don't matter.
- If necessary for an experiment requiring repeated measures, it is possible to revive a spent fly by feeding it sucrose solution. It is then best to wait at least half an hour to give it chance to process the sucrose into trehalose. Again, your fed, tethered fly may be reluctant to fly again until it is off food for several hours.
- Temperature is flies' kryptonite. The prefer cool temperature for flight (c. 15-20 degrees C). Unlike moths and bees these animals do NOT need to warm up their flight apparatus and will get quite squirrelly at temperatures over 25 degrees C. This is often a problem because the arena display generates heat. The best setting for experiments is a cool dark room.

Once you have chosen a healthy batch of flies, the next step is to tether them. In brief, a batch of flies is transferred from a bottle to a small vial that is inserted in a brass block on a cooling stage set at about 4 degrees C. The low temperature anesthetizes the flies within 30 seconds or so. The flies may then be sprinkled on the surface of the cooling stage. Choose a large, healthy-looking fly with wings nicely folded back over its abdomen for transfer to the socket of the 'sarcophagus' using a suction wand. The trickiest part of the process is coaxing a fly into proper position within the sarcophagus using a fine brush. The fly is then held gently in place by suction applied through holes in the bottom of the sarcophagus. The fly is then tethered to a fine tungsten pin using UV-activated glue. Here are some helpful tips on the tethering:

- Avoid damaging the wings with the brush, or the suction sources.
- Use only enough suction in the sarcophagus to stabilize the fly, the suction should not be so strong that the wings are pulled down off the back of the fly.
- Use an etched tungsten probe with a loop at the end to apply a droplet of glue to the tethering pin, then use the 3-D manipulator to transfer the glue from the pin to the fly.
- The most common rookie error is using too much glue. Basically, you should use the bare smallest amount that is required to hold the fly. When you are learning to tether, if you aren't losing an occasional fly because it breaks free of the tether, you are probably using too much glue.
- When gluing the head, make sure that it is oriented straight ahead, and that the head-neck are in a neutral posture, not craned up or down.
- You want the final angle between the tether pin and the long axis of the fly (the pitch angle) to be 90 degrees. This is quite critical. If the pin leans too far back, the wings will hit it when they flap; too far forward and the fly's stroke plane will not be horizontal in the flight arena as required for the optics of the wingbeat analyzer. Improper pitch alignment is the second most common rookie error.
- Make sure that the pin is bilaterally centered on the thorax, any misalignment in body roll makes the prep unusable for focusing the wingbeat analyzer.
- Hit both sides of the glue with a 20 second burst of UV light, get the tip of the gun as close to the fly as possible, but be careful not to bump the prep.
- Don't forget to relieve the sarcophagus suction before removing the tethered fly. This is another common rookie error.
- Watch through the microscope as you withdraw the fly from the sarcophagus – she may stick, and pull free from the tether – if you're watching you can correct by adding a bit more glue. Be familiar with the manipulator so that you pull the tethered fly up, instead of accidentally skewering it on its own tether.

# Optical Wingbeat Analyzer

The sensor of the wingbeat analyzer (WBA) is composed of two infrared-sensitive silicon wafers (shown below in *red*, one for each wing). An infrared LED suspended above the fly casts a shadow of the beating wings onto the sensor. An optical mask and a high gain amplifier circuit condition the sensor signals such that the final output is a voltage proportional to the position of the shadow cast by each beating wing. Increasing voltage represents increasing forward excursion of the wing, and therefore larger stroke amplitude.

Viewed from above (fly facing up the page), the shadow cast by the wings (shown in *gray*) must be laterally centered over the cutaway mask (dashed outline), a bit behind the forward edge. The size of the shadow is also important and can be adjusted by (1) moving the fly vertically, (2) moving the IR wand vertically, (3) moving the sensor surface vertically. Once these dimensional adjustments have been optimized, you should maintain them from experiment to experiment by placing the flies in the same position.

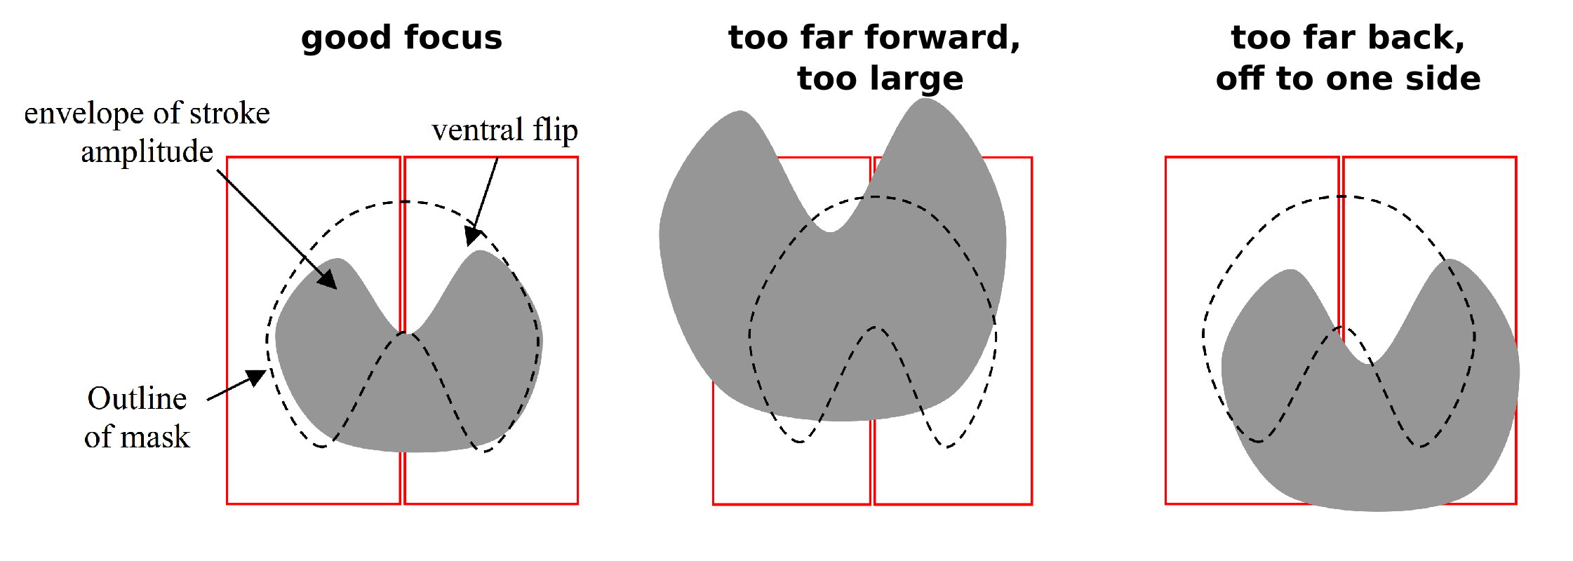
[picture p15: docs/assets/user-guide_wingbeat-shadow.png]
Wing shadow on Wingbeat Analyzer


The IR wing sensor provides the analog signal to the wingbeat analyzer, which in turn detects the frequency and amplitude of the downstroke-upstroke reversal, also called the ventral flip. Proper fly alignment over the sensor is crucial – the wingbeat analyzer is a robust instrument and will report spurious values even if the input signal is messy.

If the fly is properly focused over the sensor, then the resultant signal from the wingbeat analyzer should look like this for *each wing stroke*:

---

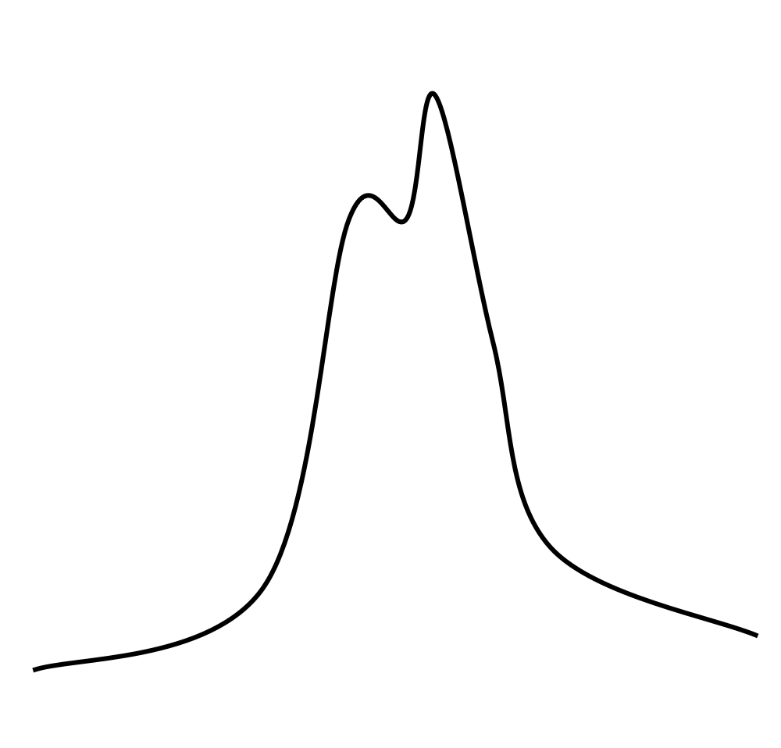
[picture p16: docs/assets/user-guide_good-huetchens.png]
Good hütchen


- Narrow waveform
- Looks like a little hat == "hütchens"
- quantal cycle-by-cycle amplitude "pops"
- Second peak larger than first

__Good hütchens!__

---

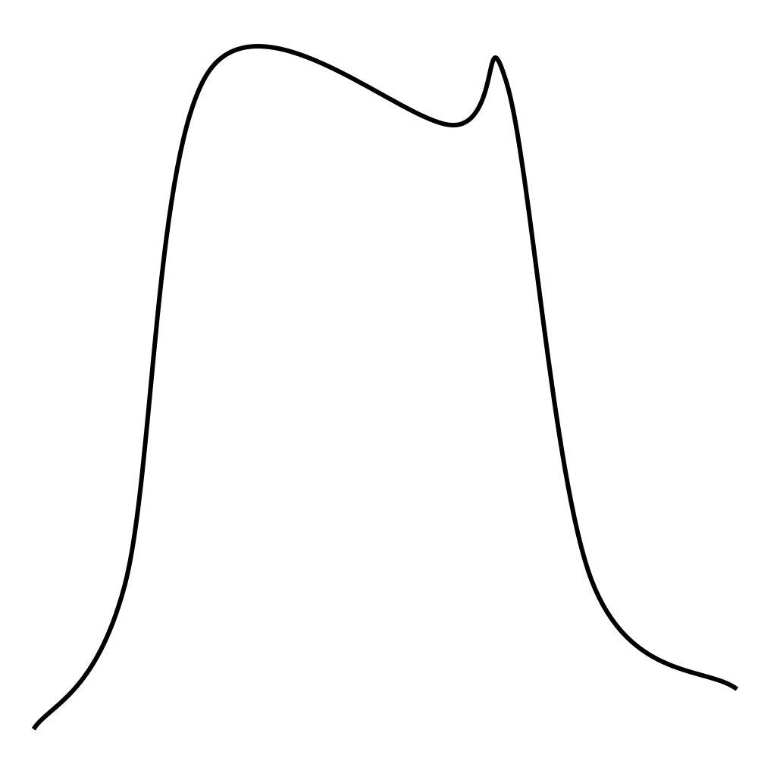
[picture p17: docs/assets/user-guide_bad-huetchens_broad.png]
Bad broad hütchen


- Broad waveform
- No cycle-by-cycle amplitude variation
- Saturated wing signal

__Bad hütchens__, more like a lüdenhut (ask MD) fly is likely too far forward over the mask

---

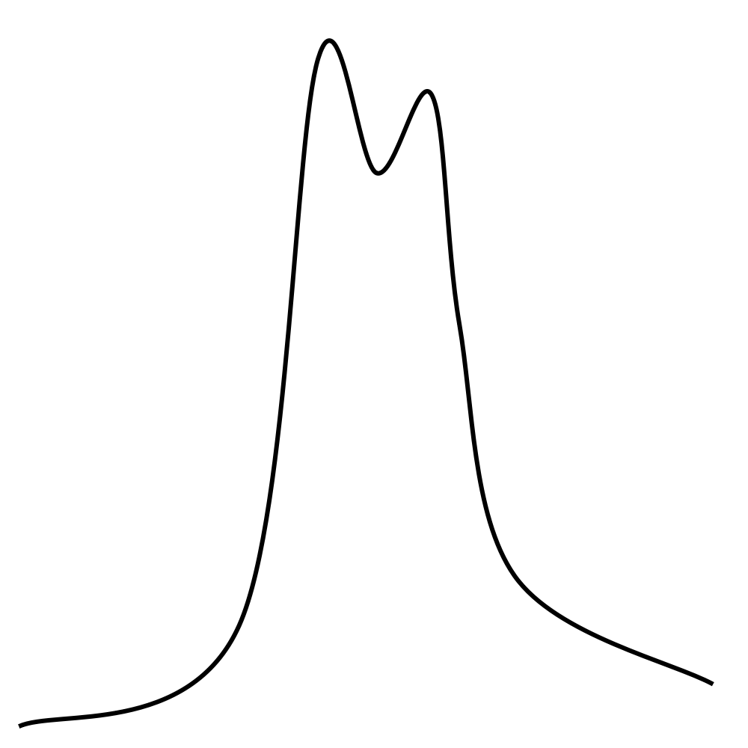
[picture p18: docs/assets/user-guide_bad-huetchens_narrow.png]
Bad narrow hütchen


- Narrow waveform
- "Quantal" cycle-by-cycle amplitude variation
- First and second peak equal height, or second is smaller

__Bad hutschienes__, fly is either too far away from the sensor surface, or too far from IR source, or both

---

The WBA tracks the analog wing sensor signal voltage, and measures a suite of parameters for each wing stroke (defined by the inflections in the hütchens occurring between the user-defined trigger and gate values):

## Inputs

- __Source__: left or right wing to set Gate and Trigger
- __Trigger__: voltage threshold to detect peak of downstroke
- __Gate__: time frame to detect peak of downstroke
- __Gain__: amplification of hutschienes – should read 2.5-3.5 Volts for standard DAQ
- __Filter__: low-pass filter analog sensor signals

## Outputs

- __Left__: analog signal from IR wing sensor
- __Right__: analog signal from IR wing sensor
- __Frequency__: stroke frequency in cycles/sec
- __L-R__: left minus right amplitude - proportional to yaw torque
- __L+R__: left plus right amplitude - proportional to thrust
- __Flip__: a brief TTL pulse synchronized with the ventral flip
- __Sync__: a TTL pulse synchronized with each wing beat - used to trigger an oscilloscope sweep

# Panel Controller

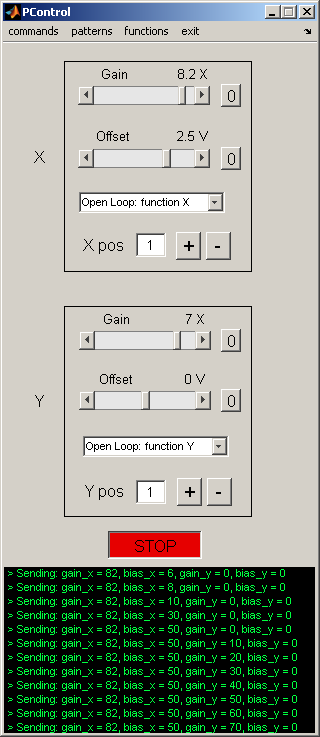
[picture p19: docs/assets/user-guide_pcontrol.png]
PControl screenshot


We tend to refer to the tiled LED array as the "arena", composed of individual "panels", the image they display as "patterns", and the black box that gives it all life the "controller."

## Quick Start

1. switch on the arena
2. insert pre-programmed compact flash card into the controller
3. switch on the controller. Verify that the left-hand green LED is on steady, verify that the two red LEDs to the right of the compact flash card are on steady
4. Start Matlab
5. in the Command Window, type `PControl`
6. Verify the serial connection between the PC and the controller, select: *commands*{:.gui-btn}->*blink LED*{:.gui-btn}, verify the blinking green LED on the controller
7. load a pattern in PControl with the menu *patterns*{:.gui-btn}->*set pattern ID*{:.gui-btn} -> set a *Pattern Index value__{:.gui-txt} (integer value)
8. set Gain to a non-zero value in the appropriate channel (*X*{:.gui-txt} or *Y*{:.gui-txt}), hit *Start*{:.gui-btn}, and *Stop*{:.gui-btn}

## Open-Loop operation

Once you have loaded a pattern to display in the arena, set the menu options in the X and Y front panel drop down menus to *Open Loop: function X*{:.gui-btn}, and *Open Loop: function Y*{:.gui-btn} (the default modes). Hit *Start*{:.gui-btn}. Play with the Gain and Offset values at will. Can you figure out what X pos and Y pos do? Program a moving pattern by using the *functions*{:.gui-btn} menu to load periodic waveforms. Now manipulate the Gain and Offset controls and hit *Start*{:.gui-btn}.

### Open Loop with an external waveform

From the *patterns*{:.gui-btn} menu, load the checkerboard pattern (hopefully, it is Pattern Index 1). Connect the output of a function generator to ADC1. From the X drop down menu, select *Position: CH5 sets X ind*{:.gui-btn}. Set the X Gain to 2.0 and hit *Start*{:.gui-btn}. Vary the controls on the function generator, and verify that the pattern moves in register with function generator output. Move the checkerboard pattern horizontally by loading an internal function in the Y-channel and selecting the drop-down menu *Open  Loop: function X*{:.gui-btn}.

## Closed-loop operation

The 'closed-loop' mode is similar to running the pattern in Open Loop with an external waveform. The only real difference is that the external function is a time-varying voltage proportional to the fly's wing amplitude (i.e. steering torque). To give the fly control over the X pattern (e.g. load a single stripe pattern, which should occupy the X channel), plug the L and R Amplitude outputs from the Wingbeat Analyzer (not to be confused with L and R Signal Out) ADC1 and ADC2 respectively. Set the X-channel drop-down menu to *Closed Loop: CH1-CH2*{:.gui-btn}. Set the X Gain to 2.0, and hit *Start*{:.gui-btn}. Use the X Offset to balance steering asymmetry. If you wish to run the Y pattern in closed-loop, connect L and R Amplitude to ADC3 and ADC 4 and set the Y-channel drop-down menu to *Closed Loop: CH3-CH4*{:.gui-btn}.

## Operation Details

### LED flight arena

A modular array of 8x8 dot matrix LED panels. Each panel is independently addressable – i.e can show a different visual pattern and can display 8 intensity levels (grayscale). In the current configuration, each LED (pixel) subtends (no more than) ~3.5 degrees at the retina. The arena should always be powered-up when the controller power switch is toggled.

### Arena controller ('black box')

Power cycle: LED arena should be on before toggling the controller power (on or off)\\
ADC1-4: inputs used to control the X and Y pattern position\\
DAC1: voltage proportional to X Position\\
DAC2: voltage proportional to Y Position

The DAC voltages will be values between 0V – 5V. The size of the voltage steps is set by the number of frames in X, Y for the current pattern (e.g. 96 frames in one channel would lead to voltage steps of 5/96 V; frame index 48 would be roughly 2.5 V). These voltage levels are remarkably consistent and can be used to recover the exact frame value for patterns of up to 500 frames (can only be done approximately for larger patterns).

### Control software running in Matlab

`PControl.m` (controller GUI) frequently calls `Panel_com.m`, a case structure of sub-functions used by the GUI. Anything the GUI can do may be executed on the command line (or in a script) with arguments to `Panel_com('argument', [value])`.  You can think of `X` and `Y` as axes of the memory buffer that stores the individual frames to display on the panels. For the arenas we constructed here, each frame of the display will be a 96 x 32 pixel bitmap (corresponding to the number of individual LED's around the azimuth and zenith, resp. of the arena). X and Y correspond to the two dimensions of the array of frames, they do NOT necessarily correspond to the coordinates of the display with respect to the fly. Here's an example: consider a vertical stripe rotating 360 degrees around the fly. This pattern requires 96 individual frames, one for each column of pixels such that if they are displayed sequentially, the pattern looks like a stripe rotating smoothly around the yaw axis. The 96 frames can be stored in `X(1:96), Y(1)`. By contrast, consider a rotating striped drum with each black-white pair composed of 8 pixels. The pattern can be stored in only 8 frames, `X(1:8), Y(1)`, and simply iterated over and over to evoke the perception of pattern moving smoothly around the yaw axis.

In general, you use PControl and associated functions to design, build, and test the patterns for experiments. Then, you execute individual functions in scripts to conduct a controlled, repeatable experiment. For example,`Panel_com` is a function with a series of different arguments – anything you do with PControl (and some things you cannot) may be programmed by `Panel_com` on the command line. Here are some examples:

```matlab
Panel_com('set_pattern_id',4);          % load pattern number 4 from compact flash
Panel_com('set_mode',[1,0]);            % closed-loop mode "Closed Loop: CH1-CH2"
Panel_com('g_level_3');                 % set all panels to grayscale level 3
Panel_com('set_position'[49, 1]);       % set the position to X=49,Y=1
Panel_com('send_gain_bias'[12,0,0,0]);  % send Gain and Bias values
Panel_com('start');                     % begin pattern motion
pause(20);                              % let the pattern run for 20 seconds
Panel_com('stop');                      % stop pattern motion
```

Panel_com commands are detailed in [Technical Appendix 1](#technical-appendix-1).

### Setting the address for a panel, or a column of panels

1. Turn controller off.
2. Unplug the I2C bus from the front of the Controller.
3. Plug a panel (or a column of panels) into the 8-pin header on the front panel of the controller. Use an 8-pin ribbon cable, and make sure to plug the LED panel in as if it were FACE DOWN coming out of the front of the controller panel.
4. Turn on controller.
5. Verify the current panel address.
6. In PControl, select *commands*{:.gui-btn}->*address*{:.gui-btn} and enter two digit values for both selections.
7. Watch the panel address change.
8. Turn off controller and remove panel.

### Building a pattern file

The display of visual patterns requires three separate steps: First, patterns must be created in numeric form most typically using a convenient program such as Matlab, and saved in a suitable format. Second, this file, containing the display information, is burned onto a flash memory card from a computer. Third, the flash memory card is inserted into the Arena Controller, and the contents are downloaded onto the panels using the Controller's software (low-level, nasty C code).

Although involving many steps, this process is straightforward, especially if using our custom Maltab functions that make this first step easier. The most complicated (for the user) part is constructing the arrays that contain the display information for the panels in the arena. In doing so it is important to keep several concepts in mind. The number of unique panels required for a display may vary. Each 8x8 pixel panel is given an identity, which is set using the procedure described above. When you power up the arena, these IDs are displayed on each panel. The identities may or may not be unique. For example, you may want an arena consisting of 12x4 panels, in which you toggle through a uniform display of grayscales. In this case every panel can have the same ID, because they will each display the identical 8x8 pixel pattern. In contrast, a standard stripe fixation experiment will require 12 unique panel IDs – enough to encode the motion of the stripe around the circle, although each column of 4 panels can have the same ID because they will always display the same pattern. In contrast, an experiment in which you control the azimuthal and elevation angle of a small spot will require that all 48 panels in your 12x4 cylinder have a unique ID. The important thing is to recognize that the way you create a pattern will depend upon the number of unique panels in your arena and their spatial distribution.

Why would you want non-unique panel IDs? Using unique panel IDs provides the most flexibility, but it does require larger patterns and those patterns will necessarily run slower – the controller must update the complete display. Any display system will have some upper bound on the rate at which it can update the display. This is an issue that should not be ignored, and in the cases where a particular experiment requires a very high frame rate, one option to consider is non-unique IDs. For example, a 12-panel pattern will achieve roughly 4 times the maximum frame rate as a 48-panel pattern.  

Assuming you are making patterns in Matlab using the utility functions written by Michael Reiser, the critical step in creating a display file is using the `make_pattern_vector` command, which operates on a `pattern` structure. The pattern structure has eight critical fields that are required before the structure may be saved in an `*.mat` file and loaded on the compact flash.

`pattern.x_num`  =  the number of frames in the 'x' channel\\
`pattern.y_num`  =  the number of frames in the 'y' channel\\
`pattern.num_panels` = number of unique panel IDs required\\
`pattern.gs_val` = grey scale value; must be either 1, 2, or 3.

`1` indicates all pixel values in `pattern.Pats` are binary (0 or 1)
`2` indicates all pixel values in `pattern.Pats` are either 0, 1, 2, or 3.
`3` indicates all pixel values in `pattern.Pats` are either 0, 1, 2, 3, 4, 5, 6, or 7.

`pattern.Pats` = This field contains the basic data for the displayed images.

Pats is a matrix of size (L,M,N,O), where:

L is the total number of pixel rows\\
M is the number of pixel columns\\
N is the number of frames in the 'x' direction, same as `pattern.x_num`\\
O is the number of frames in the 'y' direction, same as `pattern.y_num`

Thus, each entry in this LxMxNxO matrix is either one bit (for `pattern.gs_val =1`) or 2 bits (for `pattern.gs_val =2`), or 3 bits (for `pattern.gs_val =3`). Most of the work in generating a display pattern is in creating the Pats matrix. However, if a simple azimuthal shift is required (as in a yaw control experiment), the function `ShiftMatrix.m` can be used to create shifted maps required to depict the moving image.

`Pattern.Panel_map` = this is a vector or matrix that encodes the orientation of the panel IDs.

See notes above for why this is important. A simple example might be:

```matlab
Pattern.Panel_map = [1 2 3 4 5 6 7 8 9 10 11 12];
```

For a case where columns of panels display the same information. A more complicated example might be:

```matlab
A = 1:48;
pattern.Panel_map = flipud(reshape(A, 4, 12));
%  4   8   12   16   20   24   28   32   36   40   44   48
%  3   7   11   15   19   23   27   31   35   39   43   47
%  2   6   10   14   18   22   26   30   34   38   42   46
%  1   5    9   13   17   21   25   29   33   37   41   45
```

where every panel in a 12x4 panel arena needs a unique address. Panels should be addressed starting from 1, and going up to pattern.num_panels.

`pattern.BitMapIndex` = a structure that encodes the spatial panel IDs.

This field can be generated using the function, `process_panel_map.m`, which operates on pattern.Panel_map, e.g. `pattern.BitMapIndex =  process_panel_map(pattern.Panel.Map);`

`pattern.data` = final vector format of the data.

The final vector form of the data that is ready for output can be created using `Pattern.data = make_pattern_vector(pattern);`. The resulting structure is then saved as a `*.mat` file.

Here is an example Matlab script that uses these functions to create a simple panel file for a stripe fixation experiment:

```matlab
pattern.x_num = 96;             % There are 96 pixel around the display (12x8) 
pattern.y_num = 1;              % There is no vertical motion; only one frame is needed
pattern.num_panels = 12;        % This is the number of unique Panel IDs required.
pattern.gs_val = 1;             % This pattern will be binary , so grey scale code is 1;
Pats = zeros(8, 96, ...
    pattern.x_num, ...
    pattern.y_num);             % initializes the array with zeros
stripe_pattern = ...
    [ones(8,88),zeros(8,8)];    % dark pixels for the stripe 
Pats(:, :, 1, 1) = stripe_pattern;

for j = 2:96                    % use ShiftMatrixPats to rotate stripe image
    Pats(:,:,j,1) = ShiftMatrix(Pats(:,:,j-1,1),1,'r','y');
end

pattern.Pats = Pats;            % put data in structure 
pattern.panel_map = 1:1:12;     % define panel structure vector
pattern.BitMapIndex = process_panel_map(pattern);
pattern.data = make_pattern_vector(pattern);
directory_name = 'c:\matlabroot\Patterns';
str = [directory_name '\Pattern_example1']
                                % name must begin with 'Pattern_'
save(str, 'pattern');
```

## Accelerating your patterns

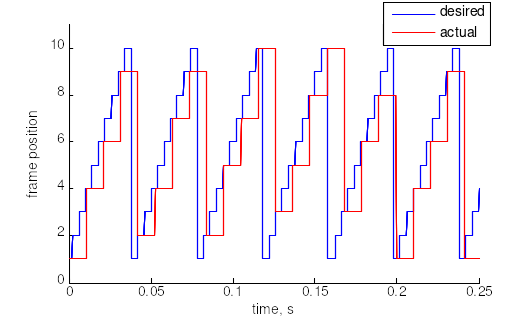
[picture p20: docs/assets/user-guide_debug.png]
speed measurement


Let's face it, we all like speed. All the fancy things that one can do with the controller will usually incur a cost—the patterns will probably display slower. By slower, we mean that the controller will spend more time refreshing an individual frame, and thus to keep up with the expected display rate (either set in open-loop by the function generator, or in closed-loop by the fly), the controller will drop frames. Suppose that we want the controller to display a 10 frame pattern at 250 Hz, but the maximum achievable frame rate is 95 Hz. The figure on the right should give a rough idea of the actual sequence of displayed frames as compared to the desired sequence.
How do you know your maximum achievable rate? Benchmark your pattern. This can be done automatically using the controller—the results are sent out through PC2 serial port. A quick and dirty benchmark can be performed by manually increasing the display rate and observing when the skip-indicating LED (green one, next to the power on LED in the middle of the controller box) starts to blink.

### How does one get more speed?

1. Simplify the pattern; either by not using grayscale, or by reducing the number of panels used.
2. Use row compression. A large number of patterns we might care to try consist of identical pattern data for all rows of the pattern. When this is the case, a row-compressed pattern will just consist of one row instead of 8. This results in a speedup factor of at least 5. To enable row compression, simply make a pattern with only one row per panel, and include the setting (`pattern.row_compression = 1;`) in the pattern making script. See example below.
3. Use 'identity' compression. The general method outlined for making and sending patterns is simple (elegant, perhaps) but should strike no one as optimal. Many patterns contain large swaths of pixels that are simply on or off. One simple shortcut that has been implemented is to simply send the row-compressed version of the panel data for a panel that corresponds to a pattern piece that is all one value (works for grayscale too!). This feature is not used at pattern making time, but rather while the pattern is running. Identity compression can be enabled by invoking: `Panel_com('ident_compress_on')` from MATLAB. Seems like a brilliant idea, why isn't it just always on? This brings up an important lesson in compression—there are no one-size-fits-all solutions. Sure this methods speeds up the pattern containing a single stripe, but consider a striped drum pattern—all of the extra comparisons needed to determine if a particular panel's piece of the pattern can be sent as a single row, will slow things down considerably and never find a compressible pattern patch.
4. Think outside the box…each pattern can probably be optimized in its own way.

Here is one more example Matlab script that creates a pattern. This one creates a grayscale sine wave grating pattern for a 48-panel display, and uses row compression. This script creates two versions of the patterns with different spatial frequencies, and stores them as Y index 1 and 2.  

```matlab
pattern.x_num = 96;         % There are 96 pixel around the display (12x8) 
pattern.y_num = 2;          % two frames of Y, at 2 different spatial frequencies
pattern.num_panels = 48;    % This is the number of unique Panel IDs required.
pattern.gs_val = 3;         % This pattern will use 8 intensity levels
pattern.row_compression = 1;
                            % size of each frame is 4x96, because of row compression. 
Pats = zeros(4, 96, ...     % initializes the array with zeros
    pattern.x_num, pattern.y_num);

% make grating patterns, periods are 120 and 60 degrees, using all 8 gscale values
Pats(:, :, 1, 1) = repmat(round(3.5*(sin((6*pi/96)*[0:95])+1) ), 4, 1);
Pats(:, :, 1, 2) = repmat(round(3.5*(sin((12*pi/96)*[0:95])+1) ), 4, 1);

for j = 2:96                % use ShiftMatrixPats to rotate stripe image
    Pats(:,:,j,1) = ShiftMatrix(Pats(:,:,j-1,1),1,'r','y');
    Pats(:,:,j,2) = ShiftMatrix(Pats(:,:,j-1,2),1,'r','y');
end

pattern.Pats = Pats;        % put data in structure 
A = 1:48;                   % define panel structure vector
pattern.Panel_map = flipud(reshape(A, 4, 12));
pattern.BitMapIndex = process_panel_map(pattern);
pattern.data = make_pattern_vector(pattern);
directory_name = 'c:\matlabroot\Patterns';
str = [directory_name '\Pattern_grating_row_comp']  
                            % name must begin with 'Pattern_'
save(str, 'pattern');
```

Programming the CF (compact flash)

1. Once you have a collection of patterns that you wish to display in the arena, put them all into C:\MatlabRoot\Panels\Patterns\. (you may in fact put them anyplace you wish, but this is the default directory).
2. Plug a Compact Flash reader into any available USB port. Insert a CF card, and verify that it appears as a drive letter. You may be prompted to format the CF, or given some error about the drive being inaccessible – IGNORE THESE.
3. Insert a CF card into the reader.
4. From PControl, select *patterns*{:.gui-btn}->*load CF*{:.gui-btn}.
5. in the Pattern Selection window, press *Add Folder*{:.gui-btn}, navigate and select the folder storing your pattern files.
6. Hit *OK*{:.gui-btn}.
7. In the Pattern Selection Tool window, verify the patterns you want to store
8. Press *Make Image*{:.gui-btn}.
9. Press *Format & Burn*{:.gui-btn}.
10. Return to the Command Window and hit *Enter*{:.gui-btn}.
11. DO NOT take out the CF card until you see a message confirming that the CF card writing is finished. In the DOS window, you will see something like *128 records in; 128 records out*{:.gui-txt}
12. Make sure the controller is switched off.
13. Pull the CF from the drive, and plug it into the arena controller.
14. Make sure that the arena is powered on, then switch on the controller.
15. PControl, click *patterns*{:.gui-btn}->*update gui*{:.gui-btn}

__Note__: to be able to access the patterns on a CF from the PControl GUI, you must be using the CF on the same machine on which it was programmed. If you load patterns onto a CF on machine A, then you may only access them on machine B by using the `Panel_com('set_pattern_id')` command.
{:.info}

# Technical Appendix 1 – User guide to the Panel_com command {#technical-appendix-1}

The `Panel_com` command allows for communication from Matlab to the arena controller. The function takes 2 values – the command and the numerical arguments (when needed).

__Note:__ It does not make sense to issue some of these commands while the controller is 'going' – i.e. updating frames. For example, if a 'All off' command is sent while the controller is updating frames – the panels will be off for maybe a few milliseconds – and then the frames will keep updating, so it might not be obvious that this command did anything.

## Useful commands

The following commands are useful for writing scripts to run experiments:

__Start__ – same as pushing the start button on the GUI, controller starts updating frames.\\
Arguments: none\\
Usage: `Panel_com('start');`\\
Special case of this command for camera trigger, usage: `Panel_com('start_w_trig');`

__Stop__ – stops the controller, pattern will freeze on last displayed frame.\\
Arguments: none\\
Usage: `Panel_com('stop');`\\
Special case of this command for camera trigger, usage: `Panel_com('stop_w_trig');`

__All off__ – sets all LEDs to off.\\
Arguments: none\\
Usage: `Panel_com('all_off');`
  
__All on__ – sets all LEDs to on.\\
Arguments: none\\
Usage: `Panel_com('all_on');`

__Set grey level__ – sets all LEDs to a greyscale level from 0 to 7:\\
Arguments: none\\
Usage: `Panel_com('g_level_0');   % set all panels to grey level 0;`\\
…\\
`Panel_com( 'g_level_7');    % set all panels to grey level 7;`

__Set pattern ID__ – sets the ID of the pattern\\
Arguments: a single value from corresponding to the pattern number (0 - # pats)\\
Usage: `Panel_com('set_pattern_id', 3);   % set to pattern 3`\\
Note: if ID used is too large – controller will crash - `Panel_com` doesn't check this

__Set controller mode__ – sets the mode for the controller's X and Y channels\\
Arguments: 2 values to set the mode for X and Y channels. 0 – open loop, 1 – closed loop, 2 – both, closed loop plus function as bias, 3 – External input sets position, 4 – Internal function generator sets position, 5 – internal function generator debug mode.\\
Usage: `Panel_com('set_mode', [0 1]); % X to open loop, Y to closed loop.`

__Set Pattern position__ – sets the position of the pattern. Controller will send this frame to panels.\\
Arguments: 2 values to set the X and Y positions, must be between 0 and num_x or num_y.\\
Usage: `Panel_com('set_position', [10 1]);`\\
Note, `Panel_com` subtracts 1 from each of these values, because in Matlab, 1 is used as the start index, and the controller uses 0. Also, if the position value is too large – frame will not be correct - `Panel_com` doesn't check this.

__Set gain and bias__ – sets the gain and bias for the X and Y channels on the controller.\\
Arguments: 4 values, 1 each to set gain_x, bias_x, gain_y, bias_y. Values must be signed integers between -127 and +127. Because of this – gain values are multiplied by 10 and bias voltages are multiplied by 20.\\
Usage: `Panel_com('send_gain_bias', [10 -10 0 20]); % sets gain_x = 1X, bias_x = -0.5 V, gain_y = 0, bias_y = 1 V (check PControl to verify this).`

__Laser on/off__ – enables/disables the laser trigger. When this is enables the controller outputs a trigger on DIO 1 and 2 (of opposite activation – one is high, the other is low), when the pattern is in a certain position, that is currently hard-coded in the controller. \\
Usage: `Panel_com('laser_on');` OR `Panel_com('laser_off');`

__Identity compression on/off__ – enables/disables a compression scheme on the controller.\\
Usage: `Panel_com('ident_compress_on');` OR `Panel_com('ident_compress_off');`

__Set trigger rate__ – sets the rate (frequency) of the optional camera trigger.\\
Arguments: 1 value, that must be an integer between 0 and 255.\\
Usage: `Panel_com('set_trigger_rate', [100]); % sets the trigger to 100 fps.`

## Commands useful for setup/debugging

__Toggle the LED__ – as a debugging measure, blinks the second green LED on the controller\\
Arguments: none\\
Usage: `Panel_com('led_tog');  % toggles controller LED`

__Controller reset__ – useful for debugging, resets the controller\\
Arguments: none\\
Usage: `Panel_com('ctr_reset') % resets the controller`

__Benchmark pattern__  - measures the average frame rate for the current pattern, spits results out on second serial ports – use in conjunction with Hyperterminal.\\
Arguments: none\\
Usage: `Panel_com('bench_pattern');`

__Reset panel__ – resets a panel, upon reset, panels show their address\\
Arguments: single value, panel address: 1-127, or 0 for all panels.\\
Usage: `Panel_com('reset', 0); %reset all panels`

__Display panel address__ – has panel display its address\\
Arguments: single value, panel address: 1-127, or 0 for all panels.\\
Usage: `Panel_com('display', 2); %have panel #2 display its address`

__ADC test__ – test the analog inputs to the controller – follow instructions in pop-up window.\\
Arguments – ADC channel to test, a number between 0 and 7\\
Usage: `Panel_com('adc_test', 3); % test ADC channel 3`

__DIO test__ – test the digital I/O lines to the controller – follow instructions in pop-up window.\\
Arguments: ADC channel to measure the DIO lines, a number between 0 and 7\\
Usage: `Panel_com('adc_test', 5); % test DIO using ADC channel 5`

__Set panel address__ – sets the address of an individual panel.\\
Arguments: 2 values, the first for current address, the second for the desired address (must be 0 – 127).\\
Usage: `Panel_com('address', [0 12]); % all panels addressed as 0, go to 12`\\
`Panel_com('address', [11 55]); % all panels addressed as 11, go to 55`\\
Note: 0 is a reserved address – all panels respond to zero.

__Send function__ – send piece of a function to the contoller.\\
Arguments: 52 byte values (integers 0 – 255). Byte 1 is identifier, 1 for X, 2 for Y, 2nd byte is the function segment number (these are 50 byte length segments), starting at zero. then 50 bytes of data. Function buffer is 1000 bytes – so 20 of these calls are needed to fill it.\\
Usage: best done with a for loop – this example is for channel X:

```matlab
for j = 0:19
        start_addr = 1 + j*50;          end_addr = start_addr + 49;
        Panel_com('send_function', [1 j scaled_func(start_addr:end_addr)]);
end
```

Note: functions must be made of signed values, between -127 and + 127, and must be scaled, so that a value of 20 corresponds to 1V [e.g. `scaled_func = round(20.*func);`].

# Technical Appendix 2 – Timing information in each operation mode {#technical-appendix-2}

To control time properly, it is essential to have a clear understanding of the operational scheme:

__Internal function generator__ is a vector of 1000 values that plays out over 20 seconds, corresponding to 50 samples/sec. Each value is a single byte, specified as a signed integer, so these can range from -127 to +127 (maybe 128). These values directly corresponds to the frame rate played out, so a 1000 value vector of 5's will produce 5 fps, if the gain is set to 1X. The __gain__ is also specified as a single byte, signed integer, so the GUI implements gains from -10 to + 10, by sending out 10 times this value – X gain of 0.5 is sent as gain_x = 5, Y gain of -2.2 is gain_y = -22, etc.

The __bias__ is also represented as 1 signed single byte integer. This value implements a virtual voltage, in the GUI, 1V is represented as the number 20 (this is only so we can use the -127 to + 127 range), this is scaled by 2.5 on the controller.
Note that in the calculations shown below, these are all integer operations implemented in C, the main significance of this is that there is no remainder kept after division (e.g. 10/3 = 3).
Each channel can operate in a few different modes, the timing of pattern display is as follows:

__mode 0, open loop__ – in this mode the internal function generator is used to set the display rate.
So the rate in open loop is calculated as (using X as the example):

```matlab
X_val = 2*function_X[function_counter];  % take the current function counter value
X_rate = ((X_val*gain_x)/10 + 5*bias_x)/2;
```

The division by 2 is implemented for added precision, but is shown here to explain the exact rate calculation. This value gives the frame rate in fps.

Ex1 – instantaneous function generator value of 10 (the default), gain_x = 1X, bias_x = 0,\\
X_rate = ( (20*10)/10 + 5*0)/2 = 10 fps

Ex2 - instantaneous function generator value of 20, gain_x = -1.5X, bias_x = 0.3 V,\\
X_rate = ( (40*-15)/10 + 5*6)/2 = -15 fps (obviously this is just 15 fps in opposite direction).

__mode 1, closed loop__ – in this mode the input voltage difference is used to set the rate, for channel X, this is CH1-CH2, for y, this is CH3-CH4. The a2d conversion digitizes 5 V with a 10 bit resolution, so 5 V maps to 1024, this range is too high, so ultimately we divide this by 4 (divide by 2 twice), so that 1 V maps to about 51 fps.

The rate is calculated as:

```matlab
X_val = (X_ADC1 - X_ADC2 )/2;
X_rate = ((X_val*gain_x)/10 + 5*bias_x)/2;
```

Ex 1 – instant. X_ADC1 = 204 (1 V), X_ADC2  = 307 (1.5V), gain_x = 2X, bias_x = 0.5 V,\\
X_val = (204 – 307)/2 = -51\\
X_rate = ( (-51*20)/10 + 5*10)/2 = -26 fps

Ex 2 - Same as above, but with gain_x = 1X, bias_x = 0.5V\\\
X_rate = ( (-51*10)/10 + 5*10)/2 = 0 fps, note that the bias has exactly cancelled out the 1/2 V input difference.

__mode 2, closed loop with bias__ – this mode is basically a combination of modes 1 and 2.

The rate is calculated as:

```matlab
X_val = (X_ADC1 - X_ADC2 )/2;
X_rate = ((X_val*gain_x)/10 + 2*function_X[function_counter] + 5*bias_x)/2;
```

__mode 3, position control mode__ – this mode is completely different from the above modes, the input voltage no longer sets the rate of the display, rather the calculation detailed will set the frame index. This may be confusing, because the notions of gain and bias have been co-opted for this function, and they are not used in exactly the same manner as above. For X, we use ADC5 to set the position, and for Y, we use ADC6. Again the digitizer is a 10 bit digitizer, so 5V maps to 1024, in this mode we do not divide by a fixed value, rather we divide by the gain. For channel x, the calculation of the frame to display is as follows:

```matlab
index_x = X_ADC5/gain_x + bias_x;
if (index_x >= x_num)  {index_x = x_num - 1;} % check if too big, x_num is # frames in x  
if (index_x <= 0)  {index_x = 0;}             % or too small
```

Ex1  – inst. input voltage is 2 V, this will convert to (2/5)*1023 = 409.\\
If gain is 1X, this will divide by 10, so index_x = 409/10 = 40.\\
If the pattern has a 40th frame, that will be displayed, otherwise it will display the last frame.

Ex2 – same 2 V input voltage, gain = 1.5X, bias = -0.5\\
index_x = 409/15 + -10 = 27 – 10 = 17, again, if there is no frame 17 then the last frame will display.

Ex3 – input is 0 V, gain is anything, bias = 1V.\\
index_x = 0/anything + 20 = 20.

__mode 4, function-based position control mode__ – this mode uses the function generator to numerically specify the current position. Gain and bias settings are irrelevant. This code shows how the current index for the x channel, index_x, is determined:

```matlab
temp_x_val = (X_pos_index + function_X[function_counter]);
if (temp_x_val >= 0) {index_x = temp_x_val%x_num; }
if (temp_x_val < 0) {index_x = x_num - ((abs(temp_x_val))%x_num); }
```

As you may notice, this implementation uses the function generator as an offset of the value stored in `X_pos_index`, which is set when a new X,Y position is sent to the controller. In this way the same function can be replayed, at different positions (in functions space), without recreating the function.

__mode 5, function generator debug mode__ – in this mode, the controller does not update the display, it plays out the function generator through the DAC outputs. The 0-5V DAC output range is used to represent a -5 to + 5 range, so the zero of the function is shifted up to 2.5 V and the range is compressed by a factor of 2 (e.g. -5V is sent out as a zero, 0V as 2.5 V, + 5V as 5V).

# Original file

This user guide is an online version of the original [flight simulator user guide](assets/flight_simulator_user_guide3.doc) (available for download in the original file format).

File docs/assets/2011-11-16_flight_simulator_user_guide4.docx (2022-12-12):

Panels User Guide

Document History:

Revisions 1-3 (Theory and Practice of Insect Flight Simulators)

Mark Frye, Michael Reiser, Michael Dickinson

Revision 4 (Panels User Guide)

Stephen Holtz, Chuntao Dan, Sung Soo Kim

Introduction

Flight arenas are a powerful tool for addressing questions about sensory control of behavior and when paired with genetic techniques an equally powerful tool for probing neural circuits. This document offers an introduction to the flight arena and should serve as a reference when starting to run experiments. It contains a brief history, an overview of some of the physical components on the arena, and documentation on arena operation from a computer (see the outline below). Troubleshooting, assembly and required downloadable content is all available on the Panels bitbucket website (https://bitbucket.org/mreiser/panels/) or the sister bitbucket site, Panels Hardware (https://bitbucket.org/mreiser/panels-hardware/). Both websites are open to the public. Throughout the document we tend to refer to the tiled LED array as the “arena”, composed of individual “panels”, the image they display as “patterns”, and the black box that gives it all life the “controller”.

Outline

The rest of the documentation will be divided into the following sections:

History and Principles of Operation – Background and principles of arena operation.

Fly Preparation – Fly housing and tethering with some helpful tips.

Hardware Overview – The common physical components of an arena.

Software Operation – Detailing the components of software for experiments.

Example Experiments – Using a simple tutorial.

Technical Appendices – For more software specific commands and operation

History and Principles of Operation

The devices and techniques described in this document owe much to approaches developed at the Max Planck Institute for Biological Cybernetics in Tübingen, Germany. This institute grew in the early 1960s around a group of four scientists: Werner Reichardt, Karl Götz, Valentino Braitenberg, and Kuno Kirschfeld, who adopted the visual system of flies as a general model system for neural processing. The term ‘Biological Cybernetics’ was used to describe to use of information theory, computer science, control theory, etc. to characterize biological systems- the term ‘reverse engineering’ is often used today to describe similar approaches. This enterprise generated a remarkable body of work, which ranged from detailed anatomical descriptions of visual system circuitry (e.g. discovery of ‘neural superposition’ in the fly) to sophisticated behavioral and physiological measurements (e.g. characterization of the lobula plate tangential cell system) to development of mathematical model of neural processing (e.g. refinement of the Hassenstein-Reichardt elementary movement detector model).

Perhaps less appreciated, was the work of Karl Götz, who developed an ingenious set of experimental methods for studying the optomotor control of flight in the fruit fly, Drosophila melanogaster. The work influenced not only the techniques described here, but also served as the direct foundation for many recent studies of visual spatial memory in Drosophila. The focus of his pioneering work was to produce visual stimuli with specific spatial and temporal properties, record the resultant behavioral responses, and then derive the intervening transfer functions. By formalizing the functional relationships between visual input and motor output, he was able to develop and test specific hypotheses about the underlying neural structures. The work was made enormously challenging because there was no “off the shelf” instrumentation at all for such experiments. Götz literally drew the plans for the devices he used throughout his career, often leaving them on the desk of the chief institute machinist before walking home in the early hours of the morning. Götz spent equal time developing ingenious ways of presenting visual stimuli to flies, and clever ways of recording, quantitatively, how the flies responded. One early device was a complex braid of fiber optic filaments that took the images displayed on an analog oscilloscope and wrapped them into a cylinder surrounding the fly. Another device employed active electromechanical feedback to record the yaw torque generated by a tethered fly. One of his more ingenious experimental techniques was a system that optically tracked the beating wings of a tethered fly, and electronically coupled these signals to rotation of a spinning glass disk, such that light projected through fish eye optics created a pattern of stripes and spots on a circular cylinder surrounding the fly. As the fly (suspended in the middle of a rotating striped drum) tried to turn left, bilateral changes in wing stroke amplitude triggered servomotors to rotate the drum to the right. Under these conditions, the fly has “closed-loop” control over the visual panorama. Using such systems, Götz pioneered studies that linked the responses of the flies visual system to its motor responses in the form of muscle activity, wing motion, and aerodynamic forces.

Recent technical advances have made flight simulators easier to build and more sophisticated, but the basic architecture remains: present a visual stimulus to the fly, record what it does (in open loop), or provide it with the opportunity of changing what it sees (in closed loop). The new systems are modular and fully programmable for visual images of varying brightness, contrast, and spatial layout.

Fly Preparation

Housing Flies

For normal, wild-type experiments, flies are generally stored in incubators at fixed temperatures on a regular light cycle. For example flies may be stored at 25 C with lights on from midnight to 4 pm. Following are some guidelines and tips on storing flies.

- Flies are crepuscular animals with activity peaks in the early morning and late afternoon – when it is cool enough to fly and light enough to see. Keep your flies on a strict light:dark cycle and perform your experiments during their crepuscular peaks. The afternoon peak is typically the most convenient. Woe to those that think such details don’t matter.
- It is quite helpful to use flies reared at low density in bottles, as opposed to high density in vials, as is unfortunately standard in genetics labs. Presorting flies a day or two before running the experiment seems to help flight time in some stocks.
- Laboratory stocks which have reproduced for some time in vials can, over time, begin to fly less reliably than freshly caught and established lines. If possible, crossing two lab stocks can results in very high performance flies.

Tethering Flies

The most critical step in collecting high quality data in a flight simulator is tethering the animals. Well-chosen, healthy, properly-tethered (i.e. ‘happy’) flies will generate hours of data each day. Crappy flies (sensu Reiser), poorly tethered are not worth putting in the arena.

Once you have chosen a healthy batch of flies (see Housing Flies and Effectively Using Flies), the next step is to tether them. In brief, a batch of flies is transferred from a bottle to a small vial that is inserted in a brass block on a cooling stage set at about 4 degrees C. The low temperature anesthetizes the flies within 30 seconds or so. The flies may then be sprinkled on the surface of the cooling stage. Choose a large, healthy-looking fly with wings nicely folded back over its abdomen for transfer to the socket of the ‘sarcophagus’ using a suction wand. The trickiest part of the process is coaxing a fly into proper position within the sarcophagus using a fine brush. The fly is then held gently in place by suction applied through holes in the bottom of the sarcophagus. The fly is then tethered to a fine tungsten pin using UV-activated glue. Here are some helpful tips on the tethering: Here are a few hints regarding the choice and care of flies in preparation for tethering:

- Avoid damaging the wings with the brush, or the suction sources.
- Avoid getting water on the fly wings or in the fly esophagus by laying down a kimwipe on the cooling stage and thoroughly wiping the surface of the sarcophagus.
- Use only enough suction in the sarcophagus to stabilize the fly, the suction should not be so strong that the wings are pulled down off the back of the fly. The shorter time the fly is under suction, the less condensation will accumulate in the sarcophagus.
- Use an etched tungsten probe with a loop at the end to apply a droplet of glue to the tethering pin, then use the 3-D manipulator to transfer the glue from the pin to the fly.
- Alternatively, the glue can be dropped onto a glass slide and the very tip of the tethering pin may be dipped in. This forms a small droplet at the end of the tether.
- The most common rookie error is using too much glue. Basically, you should use the bare smallest amount that is required to hold the fly. When you are learning to tether, if you aren’t losing an occasional fly because it breaks free of the tether, you are probably using too much glue.
- When gluing the head, make sure that it is oriented straight ahead, and that the head-neck are in a neutral posture, not craned up or down.
- You want the final angle between the tether pin and the long axis of the fly (the pitch angle) to be 90 degrees. This is quite critical. If the pin leans too far back, the wings will hit it when they flap; too far forward and the fly’s stroke plane will not be horizontal in the flight arena as required for the optics of the wingbeat analyzer. Improper pitch alignment is the second most common rookie error.
- Make sure that the pin is bilaterally centered on the thorax, any misalignment in body roll makes the prep unusable for focusing the wingbeat analyzer.
- Hit both sides of the glue with a 10 second burst of UV light, get the tip of the gun as close to the fly as possible, but be careful not to bump the prep.
- Don’t forget to relieve the sarcophagus suction before removing the tethered fly. This is another common rookie error.
- Watch through the microscope as you withdraw the fly from the sarcophagus – she may stick, and pull free from the tether – if you’re watching you can correct by adding a bit more glue. Be familiar with the manipulator so that you pull the tethered fly up, instead of accidentally skewering it on its own tether.

Effectively Using Flies

Once tethered properly, there are many other tips to get the most out of your flies during experiments:

- Animals that are 2-3 days old generally provide the best data, but older flies will work if they are healthy.
- Females fly longer and more readily than males, but this may simply be a scaling effect – female flies are much larger and thus contain greater energy reserves. Large gravid females (with big white abdomens) seem to be the most behaviorally robust. A good, healthy 1.2 mg female will fly for about 1 hour, depending on the experiment.
- It may be helpful to starve flies for 4-8 hours prior to experiments. Starved flies tend to fly more. When starving, provide a damp kimwipe in the vial or bottle so that the flies do not desiccate.
- If necessary for an experiment requiring repeated measures, it is possible to revive a spent fly by feeding it sucrose solution. It is then best to wait at least half an hour to give it chance to process the sucrose into trehalose. Again, your fed, tethered fly may be reluctant to fly again until it is off food for several hours.
- Temperature is flies’ kryptonite. They prefer cool temperature for flight (c. 15-20 degrees C). Unlike moths and bees these animals do NOT need to warm up their flight apparatus and will get quite squirrelly at temperatures over 25 degrees C. This is often a problem because the arena display generates heat. The best setting for experiments is a cool dark room.
- If possible humidity in the experimental room should be at least 50% to prevent fly desiccation and encourage flight.
- To prevent tiring during starving or while waiting to use a fly in an experiment, a small (size of the fly) piece of paper may be placed on the tethered animal. This is most practically done when the fly is held fixed by its tether in a tether holding device.
- A convenient tool for holding flies on tethers while not using them can be cut out of plastic, but a Styrofoam block weighted at the bottom suffices.

Hardware Overview

The components of a flight arena setup consist of: An LED arena, an Optical Wingbeat Analyzer, an arena controller, a data acquisition board, an oscilloscope and a computer. In this overview, the optical wingbeat analyzer, controller, arena and oscilloscope will be discussed briefly. The detailed descriptions of the components and instructions for configuration are available on the bitbucket websites listed in the introduction.

Oscilloscope

An oscilloscope is an essential tool in the flight arena for properly aligning flies. Details on the setup are available on the bitbucket websites. Just note here that in order to view useful wingbeat waveforms from the optical wingbeat analyzer, this must be properly configured as well.

Optical Wingbeat Analyzer

The sensor of the wingbeat analyzer (WBA) is composed of two infrared-sensitive silicon wafers (shown below in red, one for each wing). An infrared LED suspended above the fly casts a shadow of the beating wings onto the sensor. An optical mask and a high gain amplifier circuit condition the sensor signals such that the final output is a voltage proportional to the position of the shadow cast by each beating wing. Increasing voltage represents increasing forward excursion of the wing, and therefore larger stroke amplitude.

Viewed from above (fly facing up the page), the shadow cast by the wings (shown in gray) must be laterally centered over the cutaway mask (dashed outline), a bit behind the forward edge. The size of the shadow is also important and can be adjusted by (1) moving the fly vertically, (2) moving the IR wand vertically, (3) moving the sensor surface vertically. Once these dimensional adjustments have been optimized, you should maintain them from experiment to experiment by placing the flies in the same position.

good focus too far forward, too large too far back, off to one side

envelope of stroke amplitude

Outline

of mask

ventral flip

The IR wing sensor provides the analog signal to the wingbeat analyzer, which in turn detects the frequency and amplitude of the downstroke-upstroke reversal, also called the ventral flip. Proper fly alignment over the sensor is crucial – the wingbeat analyzer is a robust instrument and will report spurious values even if the input signal is messy.

If the fly is properly focused over the sensor, then the resultant signal from both the left and right outputs of the wingbeat analyzer should look like this for each wing stroke:

- Narrow waveform
- Looks like a little hat = = “hütchens”
- quantal cycle-by-cycle amplitude “pops”
- Second peak larger than first

Good hütchens!

- Broad waveform
- No cycle-by-cycle amplitude variation
- Saturated wing signal

Bad hütchens, more like a lüdenhut (ask MD) fly is likely too far forward over the mask

- Narrow waveform
- “Quantal” cycle-by-cycle amplitude variation
- First and second peak equal height, or second is smaller

Bad hutschienes, fly is either too far away from the sensor surface, or too far from IR source, or both

Changes to the hutchens that come from moving the fly in the arena are best learned by experimentation. If possible, align the fly while presenting a closed loop stimulus (see below) such as a dark stripe for the fly to fixate on. Some general guidelines for aligning the fly are as follows:

- If there is no amplitude variation (the hutchens are not ‘bouncy’) the fly is likely too far forward. If the amplitude seems to die down too far, increasing the current from the IR LED or moving the IR LED closer to the fly may help.
- If the left and right hutchens are not identical in shape, double check that the fly is glued symmetrically, is facing straight forward, and is centered under the LED and above the IR sensor. This can be difficult, but well worth the time spent, as it avoids later frustrations!
- If the wing hutchens disappear altogether or are saturating the wing beat analyzer, the fly is either too close to the IR LED and forward, or too far back and away from the IR LED, respectively.
- If fixing a stripe seems to be an issue for a (wild type) fly, adjusting left or right slowly and waiting for better fixation is probably necessary. By backing the fly up, or reducing the current from the IR LED, you can also reduce the difficulty of fixating. To ensure proper alignment, these settings should not be different than those used in actual experiments.

The WBA tracks the analog wing sensor signal voltage, and measures a suite of parameters for each wing stroke (defined by the inflections in the hütchens occurring between the user-defined trigger and gate values):

Inputs

- Source: left or right wing to set Gate and Trigger
- Trigger: voltage threshold to detect peak of downstroke
- Gate: time frame to detect peak of downstroke
- Gain: amplification of hutschienes – should read 2.5-3.5 Volts for standard DAQ
- Filter: low-pass filter analog sensor signals

Outputs

- Left: analog signal from IR wing sensor
- Right: analog signal from IR wing sensor
- Frequency: stroke frequency in cycles/sec
- L-R: left minus right amplitude - proportional to yaw torque
- L+R: left plus right amplitude - proportional to thrust
- Flip: a brief TTL pulse synchronized with the ventral flip
- Sync: a TTL pulse synchronized with each wing beat - used to trigger an oscilloscope sweep

Arena

LED flight arena: a modular array of 8x8 dot matrix LED panels. Each panel is independently addressable – i.e. can show a different visual pattern and can display 8 intensity levels (grayscale). In the current configuration, each LED (pixel) subtends (no more than) ~3.5 degrees at the retina. The arena should always be powered-up when the controller power switch is toggled.

Controller

The controller is the interface between the PC and the arena. There are two versions of the controller the newer, slimmer version is 3.0, some details of the controller ports are listed below.

Arena controller v 3.0 with Newest Controller Code

- ADC0: analog input in mode 1 and 2 of channel x
  - This input should be in the form of L-R. That is, with a negative gain in modes 1 and 2, a negative signal will cause a decrease in channel frame and a positive signal will cause an increase in channel frame number.
- ADC1 : analog input in mode 1 and 2 of channel y
  - This works in the same manner as ADC0
- ADC2: analog input in mode 3 of channel x
- ADC3: analog input in mode 3 of channel y
- DAC0: update current frame number (in the unit of volt) in mode 1, 2, 3, 4, and PC dumping mode of channel x, update analog output in mode 5 (debugging function generator) of channel x;
- DAC1: update current frame number (in the unit of volt) in mode 1,2,3, 4, and PC dumping mode of channel y , update analog output in mode 5 (debugging function generator) of channel y;
- DAC2: unused
- DAC3: unused
- Int0: unused;
- Int1: timing for fetching and displaying each frame when controller works in default mode and PC dumping mode. It is set to high before controller fetches a new frame data and reset to low when the controller finishes sending the data to the arena.
- Int2: laser trigger (see appendices for usage information)
- Int3: unused

Arena controller v 2.2 (‘black box’)

Power cycle –LED arena should be on before toggling the controller power (on or off)

- ADC1-4: inputs used to control the X and Y pattern position
- DAC1: voltage proportional to X Position
- DAC2: voltage proportional to Y Position
  - The DAC voltages will be values between 0V – 5V. The size of the voltage steps is set by the number of frames in X, Y for the current pattern (e.g. 96 frames in one channel would lead to voltage steps of 5/96 V; frame index 48 would be roughly 2.5 V). These voltage levels are remarkably consistent and can be used to recover the exact frame value for patterns of up to 500 frames (can only be done approximately for larger patterns).

Software Operation

Arena operation requires a MATLAB installation with a data acquisition toolbox license, the specific files necessary for interfacing with the controller can be downloaded from the bitbucket website and added to the MATLAB path. This section contains an overview of the GUI components and functions, an introduction to software control of the arena, pattern building commands, pattern acceleration discussion, and SD flash programming instructions. Many of these concepts are rehashed in the example experiment section.

MATLAB GUI Control: PControl

From the PControl GUI a lot of the arena functionality is accessible, it is a good place to start learning the system.

Quick Start

1. Switch on the arena. Panels will show addresses.
2. Insert pre-programmed SD flash card into the controller.
3. Switch on the controller. Verify that the left-hand green PWR LED is on steady. Arena will go dark.
4. Start Matlab.
5. In the Command Window, type “PControl”.
6. Verify the serial connection between the PC and the controller, select: Controller->blink LED, verify the 2nd red LED for “Memory status” blinking on the controller.
7. Load a pattern in PControl with the menu Configurations->set pattern ID -> Choose a Pattern from the dropdown menu.
8. First re-zero X and Y Gain and Offset. Set Gain to a non-zero value in the appropriate channel (X or Y), hit Start, and Stop

Open-Loop operation

Once you have loaded a pattern to display in the arena, set the menu options in the X and Y front panel drop down menus to ‘Open Loop: function X’, and ‘Open Loop: function Y’ (the default modes). Hit Start. Play with the Gain and Offset values at will. Can you figure out what X pos and Y pos do? Program a moving pattern by using the ‘functions’ menu to load periodic waveforms. Now manipulate the Gain and Offset controls and hit Start.

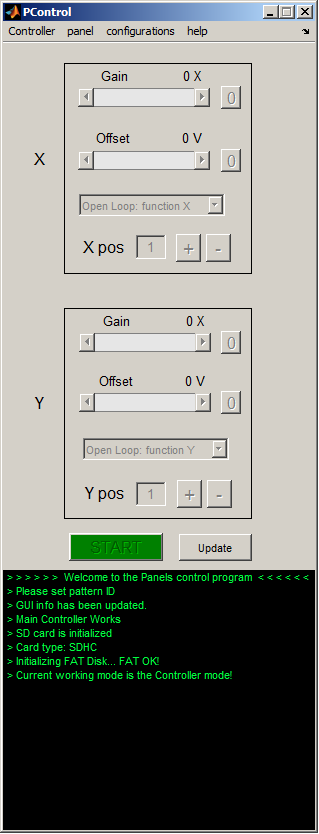
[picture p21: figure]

Open Loop with an external waveform

From the ‘patterns’ menu, load the checkerboard pattern (hopefully, it is Pattern Index 1) Connect the output of a function generator to ADC1. From the X drop down menu, select ‘Position: CH5 sets X ind’. Set the X Gain to 2.0 and hit Start. Vary the controls on the function generator, and verify that the pattern moves in register with function generator output. Move the checkerboard pattern horizontally by loading an internal function in the Y-channel and selecting the drop-down menu ‘Open Loop: function X’.

Closed-loop operation

The ‘closed-loop’ mode is similar to running the pattern in Open Loop with an external waveform. The only real difference is that the external function is a time-varying voltage proportional to the fly’s wing amplitude (i.e. steering torque). To give the fly control over the X pattern (e.g. load a single stripe pattern, which should occupy the X channel), plug the L and R Amplitude outputs from the Wingbeat Analyzer (not to be confused with L and R Signal Out) to ADC0 and ADC1 respectively. Set the X-channel drop-down menu to ‘Closed Loop: CH1-CH2’. Set the X Gain to 2.0, and hit Start. Use the X Offset to balance steering asymmetry. If you wish to run the Y pattern in closed-loop, connect L and R Amplitude to ADC2 and ADC3 and set the Y-channel drop-down menu to ‘Closed Loop: CH3-CH4’.

Introduction to software control from Matlab

PControl.m (controller GUI) frequently calls Panel_com.m, a case structure of sub-functions used by the GUI. Anything the GUI can do may be executed on the command line (or in a script) with arguments to Panel_com(‘argument’, [value]). You can think of ‘X’ and ‘Y’ as axes of the memory buffer that stores the individual frames to display on the panels. For the arenas we constructed here, each frame of the display will be a 96 x 32 pixel bitmap (corresponding to the number of individual LED’s around the azimuth and zenith, resp. of the arena). X and Y correspond to the two dimensions of the array of frames, they do NOT necessarily correspond to the coordinates of the display with respect to the fly. Here’s an example: consider a vertical stripe rotating 360 degrees around the fly. This pattern requires 96 individual frames, one for each column of pixels such that if they are displayed sequentially, the pattern looks like a stripe rotating smoothly around the yaw axis. The 96 frames can be stored in X(1:96), Y(1). By contrast, consider a rotating striped drum with each black-white pair composed of 8 pixels. The pattern can be stored in only 8 frames, X(1:8), Y(1), and simply iterated over and over to evoke the perception of pattern moving smoothly around the yaw axis.

In general, you use PControl and associated functions to design, build, and test the patterns for experiments. Then, you execute individual functions in scripts to conduct a controlled, repeatable experiment. For example, Panel_com is a function with a series of different arguments – anything you do with PControl (and some things you cannot) may be programmed by Panel_com on the command line. Here are some examples:

Panel_com('set_pattern_id',4); % load pattern number 4 from compact flash

Panel_com('set_mode',[1,0]); % closed-loop mode “Closed Loop: CH1-CH2”

Panel_com('set_position'[49, 1]); % set the position to X=49,Y=1

Panel_com('send_gain_bias'[12,0,0,0]); % send Gain and Bias values

Panel_com('start'); % begin pattern motion

pause(20); % let the pattern run for 20 seconds

Panel_com('stop'); % stop pattern motion

Panel_com commands are detailed in Technical Appendix 1.

Building a pattern file

The display of visual patterns requires three separate steps: First, patterns must be created in numeric form most typically using a convenient program such as Matlab, and saved in a suitable format. Second, this file, containing the display information, is burned onto a flash memory card from a computer. Third, the flash memory card is inserted into the Arena Controller, and the contents are downloaded onto the panels using the Controller’s software (low-level, C code).

Although involving many steps, this process is straightforward, especially if using our custom Maltab functions that make this first step easier. The most complicated (for the user) part is constructing the arrays that contain the display information for the panels in the arena. In doing so it is important to keep several concepts in mind. The number of unique panels required for a display may vary. Each 8x8 pixel panel is given an identity, which is set using the procedure described above. When you power up the arena, these IDs are displayed on each panel. The identities may or may not be unique. For example, you may want an arena consisting of 12x4 panels, in which you toggle through a uniform display of grayscales. In this case every panel can have the same ID, because they will each display the identical 8x8 pixel pattern. In contrast, a standard stripe fixation experiment will require 12 unique panel IDs – enough to encode the motion of the stripe around the circle, although each column of 4 panels can have the same ID because they will always display the same pattern. In contrast, an experiment in which you control the azimuthal and elevation angle of a small spot will require that all 48 panels in your 12x4 cylinder have a unique ID. The important thing is to recognize that the way you create a pattern will depend upon the number of unique panels in your arena and their spatial distribution.

Why would you want non-unique panel IDs? Using unique panel IDs provides the most flexibility, but it does require larger patterns and those patterns will necessarily run slower – the controller must update the complete display. Any display system will have some upper bound on the rate at which it can update the display. This is an issue that should not be ignored, and in the cases where a particular experiment requires a very high frame rate, one option to consider is non-unique IDs. For example, a 12-panel pattern will achieve roughly 4 times the maximum frame rate as a 48-panel pattern.

Assuming you are making patterns in Matlab using the utility functions written by Michael Reiser, the critical step in creating a display file is using the ‘make_pattern_vector’ command, which operates on a ‘pattern’ structure. The pattern structure has eight critical fields that are required before the structure may be saved in an ‘*.mat’ file and loaded on the flash card.

pattern.x_num = the number of frames in the ‘x’ channel

pattern.y_num = the number of frames in the ‘y’ channel

pattern.num_panels = number of unique panel IDs required

pattern.gs_val = grey scale value; must be either 1, 2, or 3.

‘1’ indicates all pixel values in pattern.Pats are binary (0 or 1)

‘2’ indicates all pixel values in pattern.Pats are either 0, 1, 2, or 3.

‘3’ indicates all pixel values in pattern.Pats are either 0, 1, 2, 3, 4, 5, 6, or 7.

pattern.Pats = This field contains the basic data for the displayed images.

Pats is a matrix of size (L,M,N,O), where:

L is the total number of pixel rows

M is the number of pixel columns

N is the number of frames in the ‘x’ direction, same as pattern.x_num

O is the number of frames in the ‘y’ direction, same as pattern.y_num

Thus, each entry in this LxMxNxO matrix is either one bit (for pattern.gs_val =1) or 2 bits (for pattern.gs_val =2), or 3 bits (for pattern.gs_val =3). Most of the work in generating a display pattern is in creating the Pats matrix. However, if a simple azimuthal shift is required (as in a yaw control experiment), the function ‘ShiftMatrix.m’ can be used to create shifted maps required to depict the moving image.

Pattern.Panel_map = this is a vector or matrix that encodes the orientation of the panel IDs.

See notes above for why this is important. A simple example might be:

Pattern.Panel_map = [1 2 3 4 5 6 7 8 9 10 11 12];

For a case where columns of panels display the same information. A more complicated example might be:

A = 1:48;

pattern.Panel_map = flipud(reshape(A, 4, 12));

% 4 8 12 16 20 24 28 32 36 40 44 48

% 3 7 11 15 19 23 27 31 35 39 43 47

% 2 6 10 14 18 22 26 30 34 38 42 46

% 1 5 9 13 17 21 25 29 33 37 41 45

where every panel in a 12x4 panel arena needs a unique address. Panels should be addressed starting from 1, and going up to pattern.num_panels. This restriction could generate confusion if you don’t use all 12 columns. For example, if you use only 7 columns with 3 rows of panels, then you have two choices. First, you may use the 4x12 panel map shown above as if you’re using all 12 columns. But it makes the pattern size larger and the speed could be slower. Instead, you may use different panel map and organize your panels accordingly as shown below.

% 3 6 9 12 15 18 21

% 2 5 8 11 14 17 20

% 1 4 7 10 13 16 19

But, you cannot use a map shown below, which is a truncated version of the 4x12 map.

% 3 7 11 15 19 23 27

% 2 6 10 14 18 22 26

% 1 5 9 13 17 21 25

pattern.BitMapIndex = a structure that encodes the spatial panel IDs.

This field can be generated using the function, ‘process_panel_map.m’, which operates on pattern.Panel_map, e.g. ‘pattern.BitMapIndex = process_panel_map(pattern);’

pattern.data = final vector format of the data.

The final vector form of the data that is ready for output can be created using ‘pattern.data =

make_pattern_vector(pattern);’ . The resulting structure is then saved as a *.mat file.

Here is an example Matlab script that uses these functions to create a simple panel file for a stripe fixation experiment:

pattern.x_num = 96; % There are 96 pixel around the display (12x8)

pattern.y_num = 1; % There is no vertical motion; only one frame is needed

pattern.num_panels = 12; % This is the number of unique Panel IDs required.

pattern.gs_val = 1; % This pattern will be binary , so grey scale code is 1;

Pats = zeros(8, 96, pattern.x_num, pattern.y_num); %initializes the array with zeros

stripe_pattern = [ones(8,88),zeros(8,8)]; %dark pixels for the stripe

Pats(:, :, 1, 1) = stripe_pattern;

for j = 2:96 %use ShiftMatrixPats to rotate stripe image

Pats(:,:,j,1) = ShiftMatrix(Pats(:,:,j-1,1),1,'r','y');

end

pattern.Pats = Pats; % put data in structure

pattern.panel_map = 1:1:12; % define panel structure vector

pattern.BitMapIndex = process_panel_map(pattern);

pattern.data = make_pattern_vector(pattern);

directory_name = 'c:\matlabroot\Patterns';

str = [directory_name '\Pattern_example1'] % name must begin with ‘Pattern_’

save(str, 'pattern');

Accelerating your patterns

Let’s face it, we all like speed. All the fancy things that one can do with the controller will usually incur a cost—the patterns will probably display slower. By slower, we mean that the controller will spend more time refreshing an individual frame, and thus to keep up with the expected display rate (either set in open-loop by the function generator, or in closed-loop by the fly), the controller will drop frames. Suppose that we want the controller to display a 10 frame pattern at 250 Hz, but the maximum achievable frame rate is 95 Hz. The figure on the right should give a rough idea of the actual sequence of displayed frames as compared to the desired sequence.

How do you know your maximum achievable rate? Benchmark your pattern. This can be done automatically using the controller—the results are sent out through PC2 serial port. A quick and dirty benchmark can be performed by manually increasing the display rate and observing when the skip-indicating LED (green one, next to the power on LED in the middle of the controller box) starts to blink.

How does one get more speed?

1) Simplify the pattern; either by not using grayscale, or by reducing the number of panels used.
2) Use row compression. A large number of patterns we might care to try consist of identical pattern data for all rows of the pattern. When this is the case, a row-compressed pattern will just consist of one row instead of 8. This results in a speedup factor of at least 5. To enable row compression, simply make a pattern with only one row per panel, and include the setting (pattern.row_compression = 1;) in the pattern making script. See example below.
3) Use ‘identity’ compression. The general method outlined for making and sending patterns is simple (elegant, perhaps) but should strike no one as optimal. Many patterns contain large swaths of pixels that are simply on or off. One simple shortcut that has been implemented is to simply send the row-compressed version of the panel data for a panel that corresponds to a pattern piece that is all one value (works for grayscale too!). This feature is not used at pattern making time, but rather while the pattern is running. Identity compression can be enabled by invoking: Panel_com('ident_compress_on') from MATLAB. Seems like a brilliant idea, why isn’t it just always on? This brings up an important lesson in compression—there are no one-size-fits-all solutions. Sure this methods speeds up the pattern containing a single stripe, but consider a striped drum pattern—all of the extra comparisons needed to determine if a particular panel’s piece of the pattern can be sent as a single row, will slow things down considerably and never find a compressible pattern patch.
4) Think outside the box…each pattern can probably be optimized in its own way.

Here is one more example Matlab script that creates a pattern. This one creates a grayscale sine wave grating pattern for a 48-panel display, and uses row compression. This script creates two versions of the patterns with different spatial frequencies, and stores them as Y index 1 and 2.

pattern.x_num = 96; % There are 96 pixel around the display (12x8)

pattern.y_num = 2; % two frames of Y, at 2 different spatial frequencies

pattern.num_panels = 48; % This is the number of unique Panel IDs required.

pattern.gs_val = 3; % This pattern will use 8 intensity levels

pattern.row_compression = 1;

% size of each frame is 4x96, because of row compression.

Pats = zeros(4, 96, pattern.x_num, pattern.y_num); %initializes the array with zeros

% make grating patterns, periods are 120 and 60 degrees, using all 8 gscale values

Pats(:, :, 1, 1) = repmat(round(3.5*(sin((6*pi/96)*[0:95])+1) ), 4, 1);

Pats(:, :, 1, 2) = repmat(round(3.5*(sin((12*pi/96)*[0:95])+1) ), 4, 1);

for j = 2:96 %use ShiftMatrix to rotate stripe image

Pats(:,:,j,1) = ShiftMatrix(Pats(:,:,j-1,1),1,'r','y');

Pats(:,:,j,2) = ShiftMatrix(Pats(:,:,j-1,2),1,'r','y');

end

pattern.Pats = Pats; % put data in structure

A = 1:48; % define panel structure vector

pattern.Panel_map = flipud(reshape(A, 4, 12));

pattern.BitMapIndex = process_panel_map(pattern);

pattern.data = make_pattern_vector(pattern);

directory_name = 'c:\matlabroot\Patterns';

str = [directory_name '\Pattern_grating_row_comp'] % name must begin with ‘Pattern_’

save(str, 'pattern');

Programming the SD Flash

1. Once you have a collection of patterns that you wish to display in the arena, put them all into C:\MatlabRoot\Panels\ Patterns\. (You may in fact put them any place you wish, but this is the default directory).
2. Plug a SD Flash card into a port, using a USB multicard reader. Verify that it appears as a drive letter. You may be prompted to format it, or given some error about the drive being inaccessible, ignore these warnings.
3. In Matlab, run PControl, and select “configurations->load pattern to SD”.
4. In the Pattern Selection window, press Add Folder, navigate and select the folder storing your pattern files.
  a. You may also individually add the patterns, if this becomes time consuming to achieve the correct order of patterns, consider naming each pattern as “Pattern_##_id” where ## is the number you wish the pattern to be and id is an identifying name. This will ensure the patterns in the folder selected are added in the correct order
5. Hit “OK”.
6. In the Pattern Selection Tool window, verify the patterns you want to store
7. Press “Make Image”.
8. Press “Format & Burn”.
9. DO NOT take out the CF card until you see a message confirming that the CF card writing is finished.
10. Make sure the controller is switched off.
11. Pull the CF from the drive, and plug it into the arena controller.
12. Make sure that the arena is powered on, then switch on the controller.

Note: to be able to access the patterns on a CF from the PControl GUI, you must be using the CF on the same machine on which it was programmed. If you load patterns onto a CF on machine A, then you may only access them on machine B by using the Panel_com(‘set_pattern_id’) command.

Example Experiments

The following instructions assume a standard arena setup with 44 panels (four rows and eleven columns), MATLAB is installed, and the”controller” folder from the Panels bitbucket website (https://bitbucket.org/mreiser/panels) is included in your MATLAB path. Going from idea to execution, this section lists the main steps and is intended as a standalone example. Note that more information on troubleshooting and setup is available on the Panels bitbucket wiki site listed in the introduction.

Plan a stimulus.

What type of experiment is desired? If there is literature already using the desired stimulus, then methods sections might be a good place to start. Even if there is not a history of your stimulus being used, this might be a good starting point if it is unclear exactly what happens in flight arena experiments. Once you have a good idea, drawing out the pattern is helpful for the next step. For the example we have chosen a simple expansion-contraction pattern, where a grating will expand from some position and contract 180° from it. For the experiment, we will be testing how the position of the expansion or contraction impacts the turning response. Specifically, we will want to test the turning response at one of three foci of expansion or contraction. [need image!!]

Design the pattern(s).

Once you know what stimulus you want to use, you must create it using a MATLAB m-file. Open a new m-file in the MATLAB editor, and name it something related to your stimulus, to keep things organized name it starting with ‘make_’ followed by a description. In order to generate a pattern from this file, a few parameters must be defined. The Software Overview section has information on the variables being set in this example; here we will reiterate the points made. For our expansion example, if thinking of the X and Y channels as axes of a memory buffer, the X channel will be all the different possible frames of expansion from one point (say, directly in front of the fly). The Y channel can then be all of the different shifts, or starting positions for this expansion. Note that each of the X-Y positions now corresponds to a state, or frame, of the arena. Here is how this is done.

First we need to populate and save a MATLAB structure called pattern and save the pattern to a file for later use (the default directory where patterns are looked for is C:\MatlabRoot\Panels\Patterns).

pattern.x_num = 96; % x is all frames of one expansion

pattern.y_num = 96; % y is different starting positions of expansion, one for each position in the arena

pattern.num_panels = 48;

pattern.gs_val = 3; % So we can play around with brightness later

pattern.row_compression = 1; % this can be used here because all of the columns in our pattern can be easily represented by a single row of the arena LEDsNow we have set the stage for our pattern. There are 96 positions in each axis of our memory buffer. Because the pattern could also be represented by one row of the panels, we can write the pattern for just one row and by using row compression, our 96 by 32 array of individual LEDs can be represented as an array of only 96 by 4 LEDs. To start, it is good form to pre-allocate a block of space for MATLAB to work with. We will call the 4-D matrix Pats.

Pats = zeros(4, 96, pattern.x_num, pattern.y_num); % Preallocate space

Next, we have to populate our blank pattern. The repmat function comes in handy here, typing help repmat in the command window gives a description of how it works. We start by populating the first frame (where x and y both = 1).

Pats(:,:,1,1) = [repmat([7*ones(4,4), 0*ones(4,4)], 1, 6),...

repmat([0*ones(4,4), 7*ones(4,4)], 1, 6)];

Now we manipulate this first frame to populate the other channels. You may first want to do the math to convince yourself you have filled up all 96 LED columns.

for i = 1:pattern.y_num

for j = 2:pattern.x_num

Pats(:,:,j,i) = simple_expansion(Pats(:,:,j-1,i), 49,96);

end

end

for g = 1:pattern.y_num;

for i = 1:pattern.x_num

Pats(:,:,i,g) = ShiftMatrix(Pats(:,:,i,1), g, 'r', 'y');

end

end

Go through these lines to understand how they populate the pattern file by first creating a filled pattern with all identical X channel expansion, and then shift the matrix one column per each Y index. Be sure to note there need not be 96 Y channels. Because the experiment only wanted to test three different starting points of expansion, the Y channels could be individually assigned to three different starting points any number of ways (one of which is increasing the shift of ShiftMatrix). Just know this is not the only way to make this pattern, or any pattern!.

pattern.Pats = Pats;

new_controller_48_panel_map = [12 8 4 11 7 3 10 6 2 9 5 1;…

24 20 16 23 19 15 22 18 14 21 17 13;…

36 32 28 35 31 27 34 30 26 33 29 25;…

48 44 40 47 43 39 46 42 38 45 41 37];

pattern.Panel_map = new_controller_48_panel_map;

pattern.BitMapIndex = process_panel_map(pattern);

pattern.data = make_pattern_vector(pattern);

directory_name = ‘C:\MatlabRoot\Panels\Patterns’;

str = [directory_name '\Pattern_expansion']

save(str, 'pattern');

The Panel_map attribute of the structure is set equal to a map of the arena panels. The given matrix is an optimized arrangement of panel IDs, corresponding to the 48Panel_4Bus arena configuration file (see below, or in appendix). Be sure that the name you give your pattern begins with “Pattern_”. Run this m-file in MATLAB to create a .mat pattern.

To play this pattern, select from the PControl gui configurations > play pattern > choose your pattern, noting the majority of the frames are black (unpopulated). We will next use a number of functions created to ease pattern creation, all of which are included in the \Panels\Pattern_tools\ folder you already included in the MATLAB path. Refer to the help, or directly to the functions for better understanding.

Understand that Pattern_expansion, when played with positive gain, will be expansion, but when played with a negative gain, will be contraction. Instead of needing to make a second pattern, we can use the one pattern twice for our desired experiment.

Putting the pattern on an SD card

The SD card is what your patterns will be played from. Plug an SD card into the PC using a USB reader or a multicard reader. Be sure it shows up under Computer as a Removable Disk, and note the drive letter is generally E. In Matlab, run PControl, and select “configurations->load pattern to SD” then in the Pattern Selection window, press Add Folder, navigate and select the folder storing your pattern files. You may also individually add the patterns, if this becomes time consuming to achieve the correct order of patterns, consider naming each pattern as “Pattern_##_id” where ## is the number you wish the pattern to be and id is an identifying name. This will ensure the patterns in the folder selected are added in the correct order. Press “Make Image” then “Burn”. If you are prompted for the drive letter at any time, type it into the prompt and press OK.

The command window should tell you if the burn was successful, once this happens remove the SD card and place it in the controller. You may need to turn the controller off and on for it to recognize the card correctly. To test the pattern, open up PControl and select configurations > set pattern ID > your pattern (from the dropdown menu). Now you can use the PControl GUI to run your pattern by selecting values and pressing the start button.

Making an experiment script

In order to have more control over patterns and settings, an experiment script will be needed. There are very few necessary settings (the same ones from the PControl GUI), and they can be changed easily using the Panel_com command. To run an experiment these are the only lines needed:

Panel_com('set_mode',Mode);

Panel_com('send_gain_bias',[Gain_X Bias_X Gain_Y Bias_Y]);

Panel_com('set_pattern_id', Pattern_ID);

Panel_com('set_position', [Ind_X Ind_Y]);

Panel_com('start')

pause(Time) % The pattern will run for this ‘Time’

Panel_com('stop')

Each of the Panel_com commands are explained in the Software Overview section and in the appendix. Some example values for each of the variables passed are as follows:

Mode = [0 0]; % Corresponds to closed loop for X and Y

Gain_X = 1;

Bias_X = 0;

Gain_Y = 0;

Bias_Y = 0;

Pattern_ID = 1; % The first pattern on the SD card

Time = 3;

Ind_X = 49; % This should center the pattern

Ind_Y = 1;

If this were saved as an experiment script it would run a pretty boring experiment, doing nothing more than what you can from the PControl GUI. What makes a more exciting experiment are more conditions, each of which may have different Gains, Biases, Patterns, X and Y starting positions, and, importantly, Modes. An easy way to do this is to store all of the relevant condition attributes in a MATLAB structure called condition. Here is an example of how this is done where the conditions differ in three ways: speed of pattern (by changing Gain_X), direction of pattern (by changing the sign of Gain_X) and starting orientation of the pattern (by changing Ind_Y). Remember our desired experiment starts expansion or contraction at one of three spots, and that by changing the direction (sign) of pattern, we switch from expansion to contraction.

speeds = [32 64 96];

time = 3;

condition_num = 1; % The first condition value

for i = 1:length(speeds)

for k = 1:2 % Positive and Negative Speed

for g = [28 36 49 % 3 Starting positions corresponding to the 3 initial expansions or contraction points

condition(condition_num).Y_ind = g;

condition(condition_num).pattern = 1; condition(condition_num).X_ind = 1;

condition(condition_num).X_gain = speeds(i);

condition(condition_num).Y_gain = 0;

condition(condition_num).X_bias = 0;

condition(condition_num).Y_bias = 0;

condition(condition_num).mode = [0 0];

condition(condition_num).time = time;

if k == 1; % Set the value to be pos

condition(condition_num).X_gain = condition(condition_num).X_gain;

else

condition(condition_num).X_gain = -condition(condition_num).X_gain;

end

condition_num = condition_num + 1;

end

end

end

num_conditions = condition_num - 1;

These for loops create the condition structure with 18 different conditions, the value of the num_conditions variable. Convince yourself by examining the structure in MATLAB, that all conditions were made and stored.

Now, by using the length of the num_conditions variable, we can loop through the different conditions by adding a for loop and some other details to the first code of this section. There is one critical component missing, a voltage encoded condition signal. In order for us to tell each condition apart when recording the experiment, each condition must be associated with some signal also recorded. Thankfully the data acquisition toolbox makes this painless, we create an analog voltage object that can encode the condition signals using a value of 1-4 volts. This example is for a standard NIDAQ board with 32-bit Windows, see below and MATLAB help for instructions on making analog output objects with other boards and OS versions.

AO = analogoutput('nidaq', 'Dev1');

chans = addchannel(AO, [0]);

Each time we switch conditions, the value of condition_num changes to encode the next condition. The command putsample from the data acquisition toolbox allows this.

putsample(AO, condition_num/(num_conditions/4))

That is the last component of the script. Here it is, from start to finish, with a few simple lines added to make it run nicely.

clear all

%% Make the condition structure

speeds = [32 64 96];

time = 3;

condition_num = 1; % The first condition value

for i = 1:length(speeds)

for k = 1:2 % Positive and Negative Speed

for g = 1:3 % 3 Starting positions

condition(condition_num).Y_ind = g;

condition(condition_num).X_ind = 1;

condition(condition_num).pattern = 1;

condition(condition_num).X_gain = speeds(i);

condition(condition_num).Y_gain = 0;

condition(condition_num).X_bias = 0;

condition(condition_num).Y_bias = 0;

condition(condition_num).mode = [0 0];

condition(condition_num).time = time;

if k == 1; % Set the value to be pos

condition(condition_num).X_gain = condition(condition_num).X_gain;

else

condition(condition_num).X_gain = -condition(condition_num).X_gain;

end

condition_num = condition_num + 1;

end

end

end

num_conditions = condition_num - 1;

%% Create an Analog Output Object (AO)

AO = analogoutput('nidaq', 'Dev1');

chans = addchannel(AO, [0]);

%% Experiment

condition_num = 1; % set this again to 1

num_reps = 3; % define the number of repititions you want

fprintf('Trial beginning')

conds_to_run = randperm(num_conditions);

fprintf(strcat('conds2run =', num2str(conds_to_run), ' \n'));

for i = 1:num_reps

for j = 1:length(conds_to_run) % for each different speed

cond_num = conds_to_run(j); % and take the values out of the condition struct

Gain_X = condition(condition_num).X_gain;

Gain_Y = condition(condition_num).Y_gain;

Bias_Y = condition(condition_num).Y_bias;

Bias_X = condition(condition_num).X_bias;

Ind_Y = condition(condition_num).Y_ind;

Ind_X = condition(condition_num).X_ind;

Pattern_ID = condition(condition_num).pattern;

Time = condition(condition_num).time;

Mode = condition(condition_num).mode;

fprintf('round %d, run %2d, cond num = %2d, speed = %2d, pause = %2d, start Y pos = %2d \n',i, j, cond_num, Gain_X, Time, Ind_Y);

disp('...next')

% Open Loop Begins

% scale condition number to fit in 0-4V range

putsample(AO, cond_num/(num_conditions/4)) Panel_com('set_mode', [Mode]); % set to open loop with Panel_com

Panel_com('set_pattern_id', Pattern_ID); Panel_com('send_gain_bias',[Gain_X Bias_Y Gain_Y Bias_Y]); Panel_com('set_position', [Ind_X Ind_Y]); Panel_com('start')

pause(Time)

Panel_com('stop')

end

end

clear AO

Important note: there are many other possible ways to set up an experiment script, here are a few:

Alternate closed loop ‘reward’ stimuli with open loop experimental stimuli. This helps to keep the fly flying and engaged

Make the experiment script into a function that can take a number of individual stimuli as input. This is useful if some conditions did not run properly during the first repetitions.

Acquiring the Data

Once the experiment script is working, and flies are ready to be run (see the Fly Preparation section), experimental data must be acquired. Data is usually acquired using a standard data acquisition board (DAQ), and a program such as LabVIEW, from National Instruments, axoscope, if you are using an Axon board, or the freeware Spikehound, developed by Gus Lott. The data acquisition toolbox in MATLAB works with all major DAQ boards, can be used in place of the GUI programs above, and has extensive help files for getting started. The programs require configuration to acquire all relevant data from the DAQ board, this is usually painless, but care should be taken to note the sampling rate each experiment is conducted at.

A typical experiment will start with some closed loop time to properly align the fly in the arena, starting the DAQ program, and then running the experiment script. If the fly stops flying during one condition, it is typically rerun before ending the DAQ program.

More detailed data acquisition instructions are available on the bitbucket sites listed in the introduction.

Preparing the Data

Depending on your DAQ program of choice you will now have a VI file from LabView, an abf file from axoscope, or a daq file from Spikehound or the Data Acquisition toolbox. Each of these formats can be loaded to the MATLAB environment with varying degrees of difficulty. In this example we will use a daq file, as this is the data acquisition native format. To read a daq file use:

Data = daqread('Filename.daq');

Note that for the proprietary axoscope format (abf files), reading into MATLAB requires a special function freely available on the MATLAB central file exchange website (www.mathworks.com/matlabcentral/fileexchange/) .This will import the file to a matrix named Data in the workspace. You can break the Data matrix into individual DAQ channels with the following strategy (if you are using the default configuration):

Left = Data(:,1); % left wing beat amplitude

Right = Data(:,2); % right wing beat amplitude

% Insert the rest of the channels here

num_conditions = 18;

condition_signal = round((num_conditions/4)* Data(:,6));

If your condition signal, or left and right wing beat amplitudes were recorded from different channels, then change the column extracted for each attribute. We must now break up the data in terms of condition, we have already recovered each condition signal in the condition_signal variable, but there are some steps required to break the data up effectively. Here is the entire script necessary to do so, note this will not fit all situations, but is representative of voltage decoding strategies. The code is heavily commented, and should be relatively transparent after some thought.

Data = daqread('Filename.daq');

Left = Data(:,1); % left wing beat amplitude

Right = Data(:,2); % right wing beat amplitude

% Insert the rest of the channels here, also needs some data from the

% experiment to be explicitly listed for later use

% From the original condition struct

num_conditions = 18;

Time = 3;

% Noted from the DAQ program settings

sample_rate = 1000;

% Recover the condition signal for the entire column of analog readings

condition_signal = round((num_conditions/4)* Data(:,6));

% establish what is a significant difference between condition signals, in

% this case 85% of the difference between two sequentials is good enough

sig_diff = (0.85*(num_condtions/4));

% create a variable with all of the Positions where the condition signal is

% significantly different (defined above)

diff_Pos = (find( abs(diff(condition_signal)) > sig_diff));

max_Pos = length(diff_Pos);

% create two arrays to define blocks of data, and make the current Position

% in the data sweep two

start_Pos = []; end_Pos = []; cur_Pos = 2;

% Search through the positions to establish blocks of data for each

% condition using both the diff_Pos and the time passing between each set

% of conditions to verify a condition change.

while cur_Pos <= max_Pos %when the current Position is less than or equal to the maximum

Pos_diff = (diff_Pos(cur_Pos) - diff_Pos(cur_Pos - 1));

range_start = diff_Pos(cur_Pos - 1);

range_end = diff_Pos(cur_Pos);

if ((Pos_diff > (Time-.15)*samp_rate)&&(Pos_diff < (Time+.15)*samp_rate))

start_Pos = [start_Pos diff_Pos(cur_Pos - 1)];

end_Pos = [end_Pos diff_Pos(cur_Pos)];

end

cur_Pos = cur_Pos + 1;

end

OL_data_length = Time*sample_rate;

% Create an empty struct, OL_Data for each condition and data line

for j = 1:num_conditions

OL_Data(j).Left = [];

OL_Data(j).Right = [];

end

% Populate the OL_Data struct for each condition, Index will correspond to

% each condition number in the original condition struct

for j = 1:(length(start_Pos))

curr_Range = start_pos(j):start_pos(j)+OL_data_length-1;

% make a condition number for each data range that corresponds to the

% actual condition number

cond(j) = round( mean(condition_signal(curr_Range)));

Index = cond(j);

OL_Data(Index).Left = [OL_Data(Index).Left; Left(curr_Range)'];

OL_Data(Index).Right = [OL_Data(Index).Right; Right(curr_Range)'];

end

% cond and OL_Data from the previous for loop need to be saved together, we

% will use a struct named fly

fly.condition = cond;

fly.OL_Data = OL_Data;

save fly fly

You now have your data broken up into several conditions ready to be graphed! More data, such as the frame index, and the wing beat frequency could be added to this data set as well.

This brings us to the end of the first sample experiment tutorial; more information is available on the bitbucket sites.

Technical Appendix 1 – User guide to the Panel_com command

The Panel_com command allows for communication from Matlab to the arena controller. The function takes 2 values – the command and the numerical arguments (when needed).

Note: It does not make sense to issue some of these commands while the controller is ‘going’ – i.e. updating frames. For example, if a ‘All off’ command is sent while the controller is updating frames – the panels will be off for maybe a few milliseconds – and then the frames will keep updating, so it might not be obvious that this command did anything.

The following commands are useful for writing scripts to run experiments:

Start – same as pushing the start button on the GUI, controller starts updating frames.

Arguments: none

Usage: Panel_com(‘start’);

Special case of this command for camera trigger, usage: Panel_com(‘start_w_trig’);

Stop – stops the controller, pattern will freeze on last displayed frame.

Arguments: none

Usage: Panel_com(‘stop');

Special case of this command for camera trigger, usage: Panel_com(‘stop_w_trig’);

All off – sets all LEDs to off.

Arguments: none

Usage: Panel_com('all_off');

All on – sets all LEDs to on.

Arguments: none

Usage: Panel_com('all_on');

Set grey level – sets all LEDs to a greyscale level from 0 to 7:

Arguments: none

Usage: Panel_com('g_level_0'); % set all panels to grey level 0;

…..

Panel_com( 'g_level_7'); % set all panels to grey level 7;

Set pattern ID – sets the ID of the pattern

Arguments: a single value from corresponding to the pattern number (0 - # pats)

Usage: Panel_com('set_pattern_id', 3); % set to pattern 3

Note: if ID used is too large – controller will crash - Panel_com doesn’t check this

Set controller mode – sets the mode for the controller’s X and Y channels

Arguments: 2 values to set the mode for X and Y channels. 0 – open loop, 1 – closed loop, 2 – both, closed loop plus function as bias, 3 – External input sets position, 4 – Internal function generator sets velocity/position, 5 – internal function generator debug mode.

Usage: Panel_com(‘set_mode’, [0 1]); % X to open loop, Y to closed loop.

Set Pattern position – sets the position of the pattern. Controller will send this frame to panels.

Arguments: 2 values to set the X and Y positions, must be between 0 and num_x or num_y.

Usage: Panel_com('set_position', [10 1]);

Note, Panel_com subtracts 1 from each of these values, because in Matlab, 1 is used as the start index, and the controller uses 0. Also, if the position value is too large – frame will not be correct - Panel_com doesn’t check this.

Set gain and bias – sets the gain and bias for the X and Y channels on the controller.

Arguments: 4 values, 1 each to set gain_x, bias_x, gain_y, bias_y. Values must be signed integers between -127 and +127. Because of this – gain values are multiplied by 10 and bias voltages are multiplied by 20.

Usage: Panel_com('send_gain_bias', [10 -10 0 20]); % sets gain_x = 1X, bias_x = -0.5 V, gain_y = 0, bias_y = 1 V (check PControl to verify this).

Laser on/off – enables/disables the laser trigger. When this is on, it enables the controller outputs a trigger on DIO 1 and 2 (of opposite activation – one is high, the other is low), when the pattern is in a certain position, that is currently hard-coded in the controller.

Panel_com('laser_on'); OR Panel_com('laser_off');

Identity compression on/off – enables/disables a compression scheme on the controller. Panel_com('ident_compress_on'); OR Panel_com('ident_compress_off');

Set trigger rate – sets the rate (frequency) of the optional camera trigger.

Arguments: 1 value, that must be an integer between 0 and 255.

Usage: Panel_com('set_trigger_rate', [100]); % sets the trigger to 100 fps.

Send laser pattern – Use the laser switch with a user set pattern.
Arguments: Panel_com('send_laser_pattern',pattern);

Pattern, a numerical array with 96 elements whose value is either 0 or 1.
Usage: Panel_com('send_laser_pattern' [ones(1,24),zeros(1,24),ones(1,24),zeros(1,24)]);

Commands useful for setup/debugging -

Toggle the LED – as a debugging measure, blinks the second green LED on the controller

Arguments: none

Panel_com('led_tog'); % toggles controller LED

Controller reset – useful for debugging, resets the controller

Arguments: none

Usage: Panel_com('ctr_reset') % resets the controller

Benchmark pattern - measures the average frame rate for the current pattern, spits results out on second serial ports – use in conjunction with Hyperterminal.

Arguments: none

Usage: Panel_com('bench_pattern');

Reset panel – resets a panel, upon reset, panels show their address

Arguments: single value, panel address: 1-127, or 0 for all panels.

Usage: Panel_com('reset', 0); %reset all panels

Display panel address – has panel display its address

Arguments: single value, panel address: 1-127, or 0 for all panels.

Usage: Panel_com('display', 2); %have panel #2 display its address

ADC test – test the analog inputs to the controller – follow instructions in pop-up window.

Arguments – ADC channel to test, a number between 0 and 7

Usage: Panel_com(‘adc_test’, 3); % test ADC channel 3

DIO test – test the digital I/O lines to the controller – follow instructions in pop-up window.

Arguments: ADC channel to measure the DIO lines, a number between 0 and 7

Usage: Panel_com(‘adc_test’, 5); % test DIO using ADC channel 5

Set panel address – sets the address of an individual panel.

Arguments: 2 values, the first for current address, the second for the desired address (must be 0 – 127).

Usage: Panel_com(‘address’, [0 12]); % all panels addressed as 0, go to 12

Panel_com(‘address’, [11 55]); % all panels addressed as 11, go to 55

Note: 0 is a reserved address – all panels respond to zero.

Set position function id – set the function generator to work in a position mode.

Arguments: 2 values, the first for selection of x or y (0 or 1 respectively), the second for the function id.

Usage: Panel_com(‘set_posfunc_id’, [1 9]); % sets x function generator with function id 9

Panel_com(‘set_posfunc_id’, [2 7]); % sets y function generator with function id 7

Note: See technical appendix 2 for more detail

Set velocity function id – set the function generator to work in a velocity mode.

Arguments: 2 values, the first for selection of x or y (0 or 1 respectively), the second for the function id.

Usage: Panel_com(‘set_velfunc_id’, [1 9]); % sets x function generator with function id 9

Panel_com(‘set_velfunc_id’, [2 7]); % sets y function generator with function id 7

Note: See technical appendix 2 for more detail

Set frequency of function – set the frequency of the function generator of x or y.

Arguments: takes a value between 0 and 500. Problems may arise if not using multiples of 50.

Usage: Panel_com(‘set_funcx_freq’, 50); % sets the frequency of x function generator 50.

Panel_com(‘set_funcy_freq’, 100); % sets the frequency of y function generator 100.

Note: See technical appendix 2 for more detail

Send function – send piece of a function to the contoller.

Arguments: 52 byte values (integers 0 – 255). Byte 1 is identifier, 1 for X, 2 for Y, 2nd byte is

the function segment number (these are 50 byte length segments), starting at zero. then 50 bytes of data. Function buffer is 1000 bytes – so 20 of these calls are needed to fill it.

Usage: best done with a for loop – this example is for channel X.

for j = 0:19

start_addr = 1 + j*50; end_addr = start_addr + 49;

Panel_com('send_function', [1 j scaled_func(start_addr:end_addr)]);

end

Note: functions must be made of signed values, between -127 and + 127, and must be scaled, so that a value of 20 corresponds to 1V [e.g. scaled_func = round(20.*func); ].

Show bus number – displays the bus numbers in the arena.

Arguments: none

Usage: Panel_com(‘show_bus_number’);

Set arena config – set the current arena configuration file, searches the SD card for available options.

Arguments: see usage

Usage: From the PControl GUI, configurations > set arena config.

This works similarly to setting the current pattern ID. A dropdown menu displays the configuration files to loaded on the SD card to select for use with the current arena.

Load config to SD – loads an arena configuration file to the SD card, the default directory is Panel_Controller\arena_config\ .

Arguments: see usage

Usage: From the PControl GUI, configurations > load config to SD

This works similarly to loading patterns and functions to SD card. Once configuration files (mat files) have been added to the Configuration List window by Add or Add folder, selecting ‘load config’ will write the files to an SD card. Progress will be displayed in the command window. Note that the same limitation with pattern writing applies for configuration files. Other computers will not be able to read these names in the PControl GUI.

Edit arena config – make or edit a set of arena addresses to save or load to an SD card.

Arguments: see usage

Usage: From the PControl GUI, configurations > edit arena config.

An interactive arena configuration table allows creation and saving of a custom panel arrangement. Because there are 4 busses and the ability to skip an address, each panel ID can be assigned one of five values, 0-4. As noted on the arena_config table:

Channel 0 - No panel/skip this address

Channel 1 – assign to bus 0

Channel 2 – assign to bus 1

Channel 3 – assign to bus 2

Channel 4 – assign to bus 3

This configuration should be compatible with the map used to create patterns. For example, the assignments in the config file should be to numbers that exist in the pattern map.

Version – display the Panel Controller version number in an open PControl GUI.

Arguments: none

Usage: Panel_com(‘get_version’); From the PControl GUI, help > version

Technical Appendix 2 – Operational Mode Details

To control time properly, it is essential to have a clear understanding of the operational scheme:

Internal function generator is a vector of 1000 values that plays out over 20 seconds, corresponding to 50 samples/sec. Each value is a single byte, specified as a signed integer, so these can range from -127 to +127 (maybe 128). These values directly corresponds to the frame rate played out, so a 1000 value vector of 5’s will produce 5 fps, if the gain is set to 1X. The gain is also specified as a single byte, signed integer, so the GUI implements gains from -10 to + 10, by sending out 10 times this value – X gain of 0.5 is sent as gain_x = 5, Y gain of -2.2 is gain_y = -22, etc.

The bias is also represented as 1 signed single byte integer. This value implements a virtual voltage, in the GUI, 1V is represented as the number 20 (this is only so we can use the -127 to + 127 range), this is scaled by 2.5 on the controller.

Note that in the calculations shown below, these are all integer operations implemented in C, the main significance of this is that there is no remainder kept after division (e.g. 10/3 = 3).

Each channel can operate in a few different modes, the timing of pattern display is as follows:

mode 0, open loop – in this mode the internal function generator is used to set the display rate.

So the rate in open loop is calculated as (using X as the example):

X_val = 2*function_X[function_counter]; % take the current function counter value

X_rate = ((X_val*gain_x)/10 + 5*bias_x)/2;

The division by 2 is implemented for added precision, but is shown here to explain the exact rate calculation. This value gives the frame rate in fps.

Ex1 – instantaneous function generator value of 10 (the default), gain_x = 1X, bias_x = 0,

X_rate = ( (20*10)/10 + 5*0)/2 = 10 fps

Ex2 - instantaneous function generator value of 20, gain_x = -1.5X, bias_x = 0.3 V,

X_rate = ( (40*-15)/10 + 5*6)/2 = -15 fps (obviously this is just 15 fps in opposite direction).

mode 1, closed loop – in this mode the input voltage difference is used to set the rate, for channel X, this is CH1-CH2, for y, this is CH3-CH4. The a2d conversion digitizes 5 V with a 10 bit resolution, so 5 V maps to 1024, this range is too high, so ultimately we divide this by 4 (divide by 2 twice), so that 1 V maps to about 51 fps.

The rate is calculated as:

X_val = (X_ADC1 - X_ADC2 )/2;

X_rate = ((X_val*gain_x)/10 + 5*bias_x)/2;

Ex 1 – instant. X_ADC1 = 204 (1 V), X_ADC2 = 307 (1.5V), gain_x = 2X, bias_x = 0.5 V,

X_val = (204 – 307)/2 = -51

X_rate = ( (-51*20)/10 + 5*10)/2 = -26 fps

Ex 2 - Same as above, but with gain_x = 1X, bias_x = 0.5V

X_rate = ( (-51*10)/10 + 5*10)/2 = 0 fps, note that the bias has exactly cancelled out the 1/2 V input difference.

mode 2, closed loop with bias – this mode is basically a combination of modes 1 and 2.

The rate is calculated as:

X_val = (X_ADC1 - X_ADC2 )/2;

X_rate = ((X_val*gain_x)/10 + 2*function_X[function_counter] + 5*bias_x)/2;

mode 3, position control mode – this mode is used in an experiment where online control of the frame position is required by some other equipment rather than the Wing Beat Analyzer. You can dynamically determine the position of frame as the experiment goes on.

This mode uses ADC4 and ADC5 (in an older controller, they are ADC5 and ADC6) to determine the position of x and y frame respectively. To utilize the full capacity of voltage range that the controller can accept, it uses gain_x and bias_x in a very different way from mode0~2. Users must understand the detailed computation to correctly determine the input voltage.

The digitizer is a 10 bit digitizer, so 5V maps to 1024, in this mode we do not divide by a fixed value, rather we divide by the gain. For channel x, the calculation of the frame to display is as follows:

index_x = X_ADC5/gain_x + bias_x; // Note that the division drops remainder.

if (index_x >= x_num) {index_x = x_num - 1;} //check if too big, x_num is # frames in x

if (index_x <= 0) {index_x = 0;} //or too small

Ex1 – inst. input voltage is 2 V, this will convert to (2/5)*1023 = 409. (Integer division drops the remainder.)

If gain is 1X, this will divide by 10, so index_x = 409/10 = 40.

If the pattern has a 40th frame, that will be displayed, otherwise it will display the last frame.

Ex2 – same 2 V input voltage, gain = 1.5X, bias = -0.5

index_x = 409/15 + -10 = 27 – 10 = 17, again, if there is no frame 17 then the last frame will display.

Ex3 – input is 0 V, gain is anything, bias = 1V.

index_x = 0/anything + 20 = 20.

For best resolution, the user should determine the gain and the bias so that the frame index covers the maximum span of 5V. Usually, the bias is set to zero to avoid confusion, and only gain is calculated. The following Matlab routine generates reasonable voltage values for each x_frame index and the gain.

function index_voltage_map = index_to_voltage_converter(x_num, y_num)

gx = round( 1000/x_num ); % instead of 1023 for margin

if gx>100

gx=100;

elseif gx<1

gx=1;

end

gy = round( 1000/y_num );

if gy>100

gy = 100;

elseif gy<1

gy=1;

end

index_voltage_map.x = idx2volt([0:x_num-1],gx);

index_voltage_map.y = idx2volt([0:y_num-1],gy);

index_voltage_map.gain_x = gx;

index_voltage_map.bias_x = 0;

index_voltage_map.gain_y = gy;

index_voltage_map.bias_y = 0;

function mx = idx2volt(x, g)

for xi=1:length(x)

n = x(xi);

m = 0;

%m = floor(m*100)/100;

ok = 0;

mo=[];

while ~ok

m = m+0.001;

ttmp = floor(m/5*1023*10)/10/g; % 10V=4095, 5V limit, and X_ADC1 = analogRead(4)/2; index_x = X_ADC1/gain_x + bias_x;

% if ttmp > n+0.4

% ok=1;

% mx(1,xi) = m;

% end

if floor(ttmp)==n

mo(end+1) = m;

elseif floor(ttmp)==n+1

ok=1;

mx(1,xi) = median(mo);

end

end

end

mode 4, function-based position control mode – this mode is very useful if you want to present a preset sequence of patterns. Theoretically, you may use both mode 3 and mode 4 for the same purpose, but mode 3 has an electrical noise issue (on the communication using BNC cables), when you use too many frames (>200 or 300), that could affect your experiment at the expense of online control capability. Mode 4 is different in the sense that you cannot control the pattern online, but you can use the maximum number of frames that the system allows without any frame jittering caused by electrical noise. Mode 4 uses the function generator to numerically specify the current position. Gain and bias settings are irrelevant.

The following Matlab code generates functions.

func = [0 1 2 3 4 5 6 7 …… 95 ]; % sweeps from the first frame to 96th frame.

% Note that the actual position depends on the initial position. See below.

save(‘position_function_my_sweep’, 'func');

Note that the prefix ‘position_function’ is used. You must use this prefix to correctly apply your function in the system. Also note that the variable name is ‘func’. If you use a different name, then the provided utility function cannot convert it to a proper bit stream.

Next, you open PControl and select the menu “load function to SD”. Add ‘position_function_my_sweep’, make image and burn it to the SD card.

If you use PControl for your experiment, you can use this function by selecting ‘set position function’ in the menu, then pick mode 4 (Position: function X (or Y) sets ind.) in the drop down menu.

If you use Matlab command line, the following sequence of commands should be applied.

Freq = 50; % There is a report that Freq should be multiple of 50

% to avoid freezing.

xfid = 1; % the id of position function starts from 1.

% So if you have only one function, it should be 1.

% If you have more, it increment by 1.

yfid = 1; % Assuming that you have another function for y,

% though you may use the same function as x. In this case,

% if y_num is smaller than 96, it will be wrapped.

% E.g., y_num is 10, then function value of 33 will be

% postion 3 for y frame. See below for implementation.

Pattern_id = 3; % some random value as an example.

init_pos = [3 2]; % The actual position of x, y frame is

% offset by these numbers.

Panel_com('set_funcx_freq' , Freq);

Panel_com('set_posfunc_id', [1, xfid]);

Panel_com('set_funcy_freq' , Freq);

Panel_com('set_posfunc_id', [2, yfid]);

Panel_com('set_mode', [4 4]); % both x and y are using mode 4 here,

% but you don’t have to.

Panel_com('send_gain_bias', [0 0 0 0]);

Panel_com('set_pattern_id', Pattern_id);

Panel_com('set_position', init_pos); % offset the position functions.

% Caution: Panel_com automatically subtract 1 from init_pos.

Panel_com('start')

This code shows how the current index for the x channel, index_x, is determined:

temp_x_val = (X_pos_index + function_X[function_counter]);

if (temp_x_val >= 0) {index_x = temp_x_val%x_num; }

if (temp_x_val < 0) {index_x = x_num - ((abs(temp_x_val))%x_num); }

As you may notice, this implementation uses the function generator as an offset of the value stored in X_pos_index, which is set when a new X,Y position is sent to the controller. In this way the same function can be replayed, at different positions (in functions space), without recreating the function. Also note that the ‘%’ operation in C-code causes wrapping if the function value is larger than x_num.

mode 5, function generator debug mode – in this mode, the controller does not update the display, it plays out the function generator through the DAC outputs. The 0-5V DAC output range is used to represent a -5 to + 5 range, so the zero of the function is shifted up to 2.5 V and the range is compressed by a factor of 2 (e.g. -5V is sent out as a zero, 0V as 2.5 V, + 5V as 5V).

Technical Appendix 3 – System setup guide

The components required to effectively perform an experiment in a visual flight arena are the controller, wingbeat analyzer (WBA), data acquisition module, oscilloscope, PC, and display panels. Directions and software for many of these components are available at https://bitbucket.org/mreiser/panels/wiki/Home

This document outlines the proper configuration of these components for a typical open- or closed-loop flight experiment. Once this setup works, you may change the configuration depending on your particular experiments.

Basic Components:

1. The flight arena consists of a circular array of 8x8 dot matrix displays of LEDs with additional electronics to drive the display.

2. The data acquisition module is the nidaq, or National Instruments Data Acquisition Device. In this case, the nidaq is a NI USB-6229 BNC Multifunction DAQ. This model has 16 analog inputs, 4 analog outputs, 8 DIOs and 2 user defined BNC terminals—more information about this device is available at http://sine.ni.com/nips/cds/view/p/lang/en/nid/203866.

3. The controller is a microprocessor circuit custom designed to operate the flight arena. The controller communicates with a PC through a serial port and to the panels using a rapid serial interface.

4. The wingbeat analyzer (WBA) measures the frequency and amplitude of the fly wing stroke. It also computes the sum and difference of the amplitudes of the left and right wings. This device is custom built by JFI Electronics at the University of Chicago. You may purchase the photo detector from the same vendor or assemble by yourself. You may also use any kind of IR LED for illumination. A typical IR LED is Emitter IR 880NM 8DEG TO-46 - PDI-E803 (PDI-E803-ND from Digi-key). Finally, a use of proper IR long pass filter is essential to avoid ambient light noise. Typically, RG-780 Long Pass Filter 1 inch Dia (NT32-757) is used.

5. The PC is used to display patterns on the flight arena and record data through the nidaq. The PC must be capable of running Matlab as well as a data acquisition program such as Spikehound (freely available), Matlab data acquisition toolbox or AxoScope. It must have at least two USB and one serial ports (one USB and one serial ports for older controllers).

6. An oscilloscope with three input channels and an external trigger will suffice.

Connectivity:

Controller | ADC0 | WBA L
Controller | ADC1 | WBA R
Controller | DAC0 | Nidaq Input 3
Controller | DAC1 | Nidaq Input 4
Controller | PC1 USB | PC USB
Controller | I2C | Serial Port to Arena
Nidaq | Analog Input 0 | WBA - L
Nidaq | Analog Input 1 | WBA - R
Nidaq | Analog Input 2 | WBA - Frequency
Nidaq | Analog Input 3 | Controller DAC0
Nidaq | Analog Input 4 | Controller DAC1
Nidaq | Analog Input 5 | WBA - L-R
Nidaq | Analog Input 6 | Analog Output 1
Nidaq | USB Output | PC
Nidaq | Analog Output 1 | Analog Input 6
Wingbeat Analyzer | WBA L | Controller ADC0, Nidaq AI 0
Wingbeat Analyzer | WBA R | Controller ADC1, Nidaq AI 1
Wingbeat Analyzer | Signal Out L | Oscilloscope Ch 1, Speakers
Wingbeat Analyzer | Signal Out R | Oscilloscope Ch 2, Speakers
Wingbeat Analyzer | WBA L-R | Oscilloscope Ch 3, Nidaq AI 5
Wingbeat Analyzer | SYNC (-TTL) | Oscilloscope Ext Trig
Wingbeat Analyzer | LED Out | IR LED on Flight Arena
Wingbeat Analyzer | Photo detector | Photo detector on Flight Arena
Wingbeat Analyzer | Frequency | Nidaq AI 2
Oscilloscope | Channel 1 | WBA L
Oscilloscope | Channel 2 | WBA R
Oscilloscope | Channel 3 | WBA L-R
Oscilloscope | Ext Trig | WBA SYNC (-TTL)
Flight Arena | Serial Port | Controller I2C
Flight Arena | Photodetector | WBA Photodetector
Flight Arena | LED | WBA LED Out
PC | USB | Nidaq
PC | USB | Controller PC1 USB

Note that ADC0~3 corresponds to ADC1~4 for older controllers. Similarly, DAC0~3 to DAC1~4 and INT0~3 to INT1~4.

If you want to use mode 3 in the new controller, you should make a custom connector to the parallel port on the back of the controller, because ADC4 and 5 are not readily available in the front panel of the controller. See https://bitbucket.org/mreiser/panels-hardware/wiki/Controller for more details.

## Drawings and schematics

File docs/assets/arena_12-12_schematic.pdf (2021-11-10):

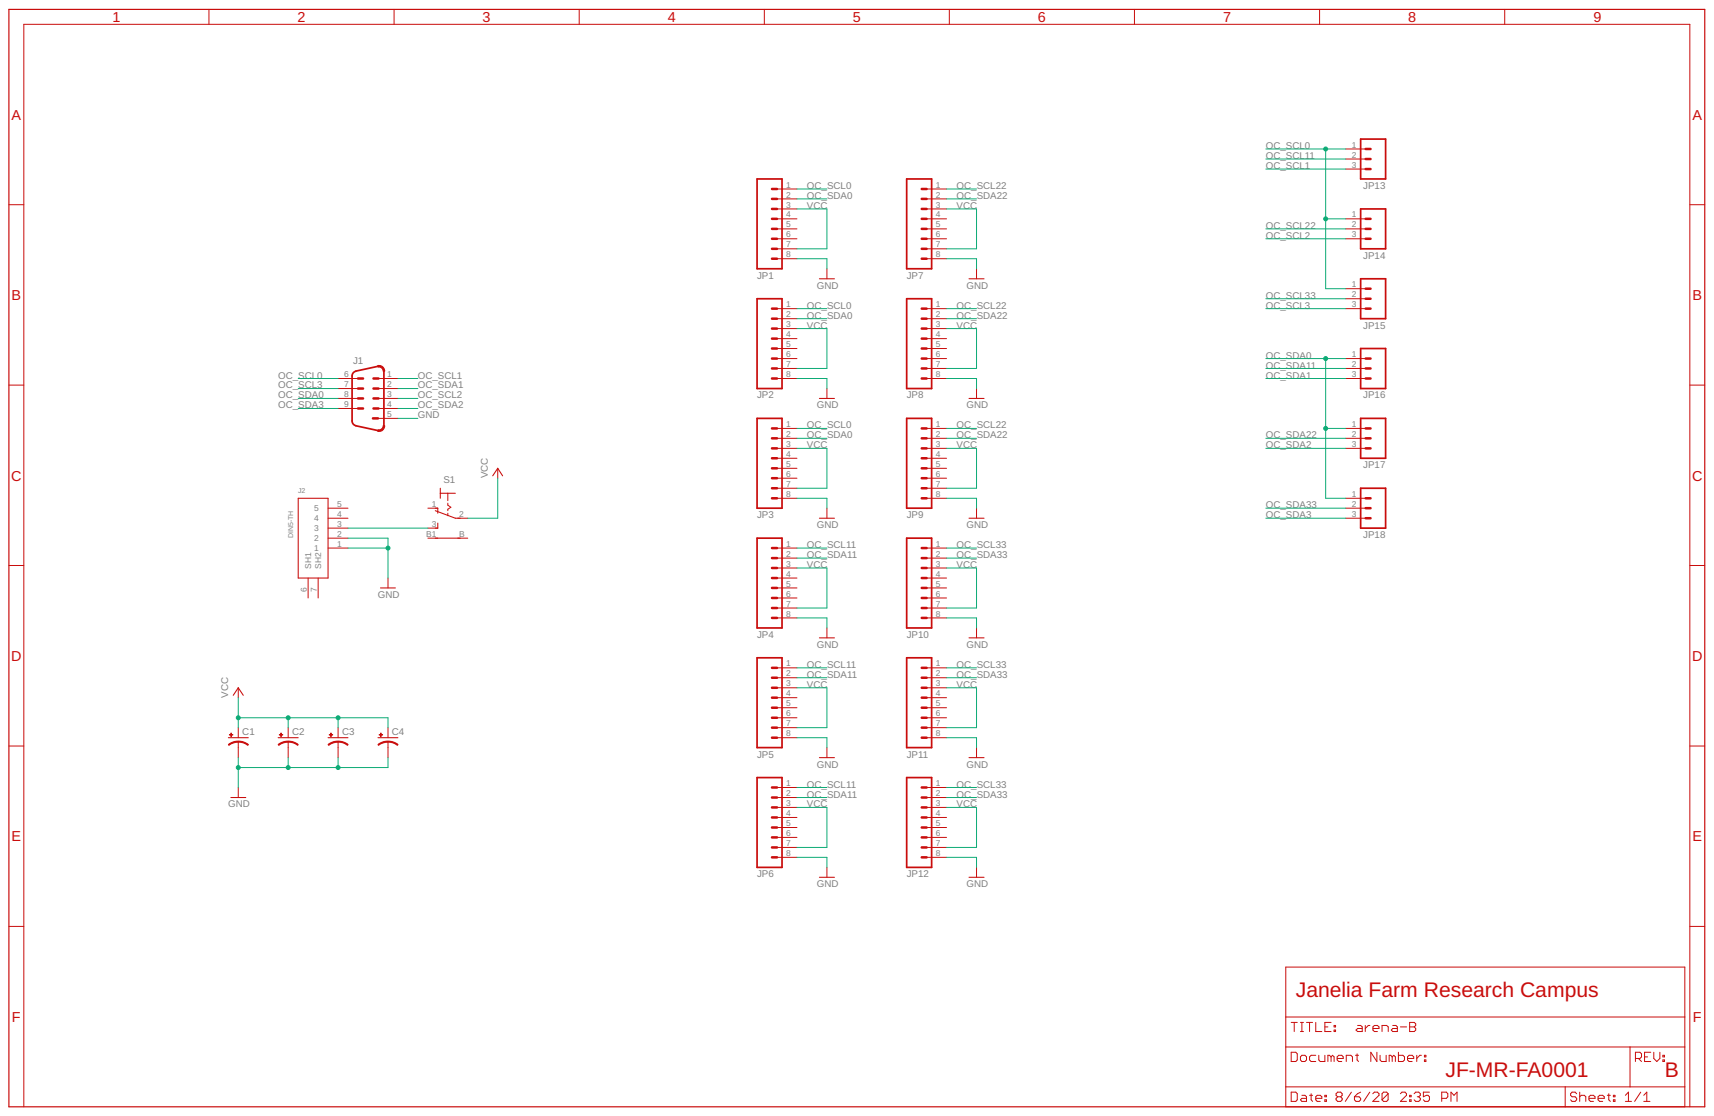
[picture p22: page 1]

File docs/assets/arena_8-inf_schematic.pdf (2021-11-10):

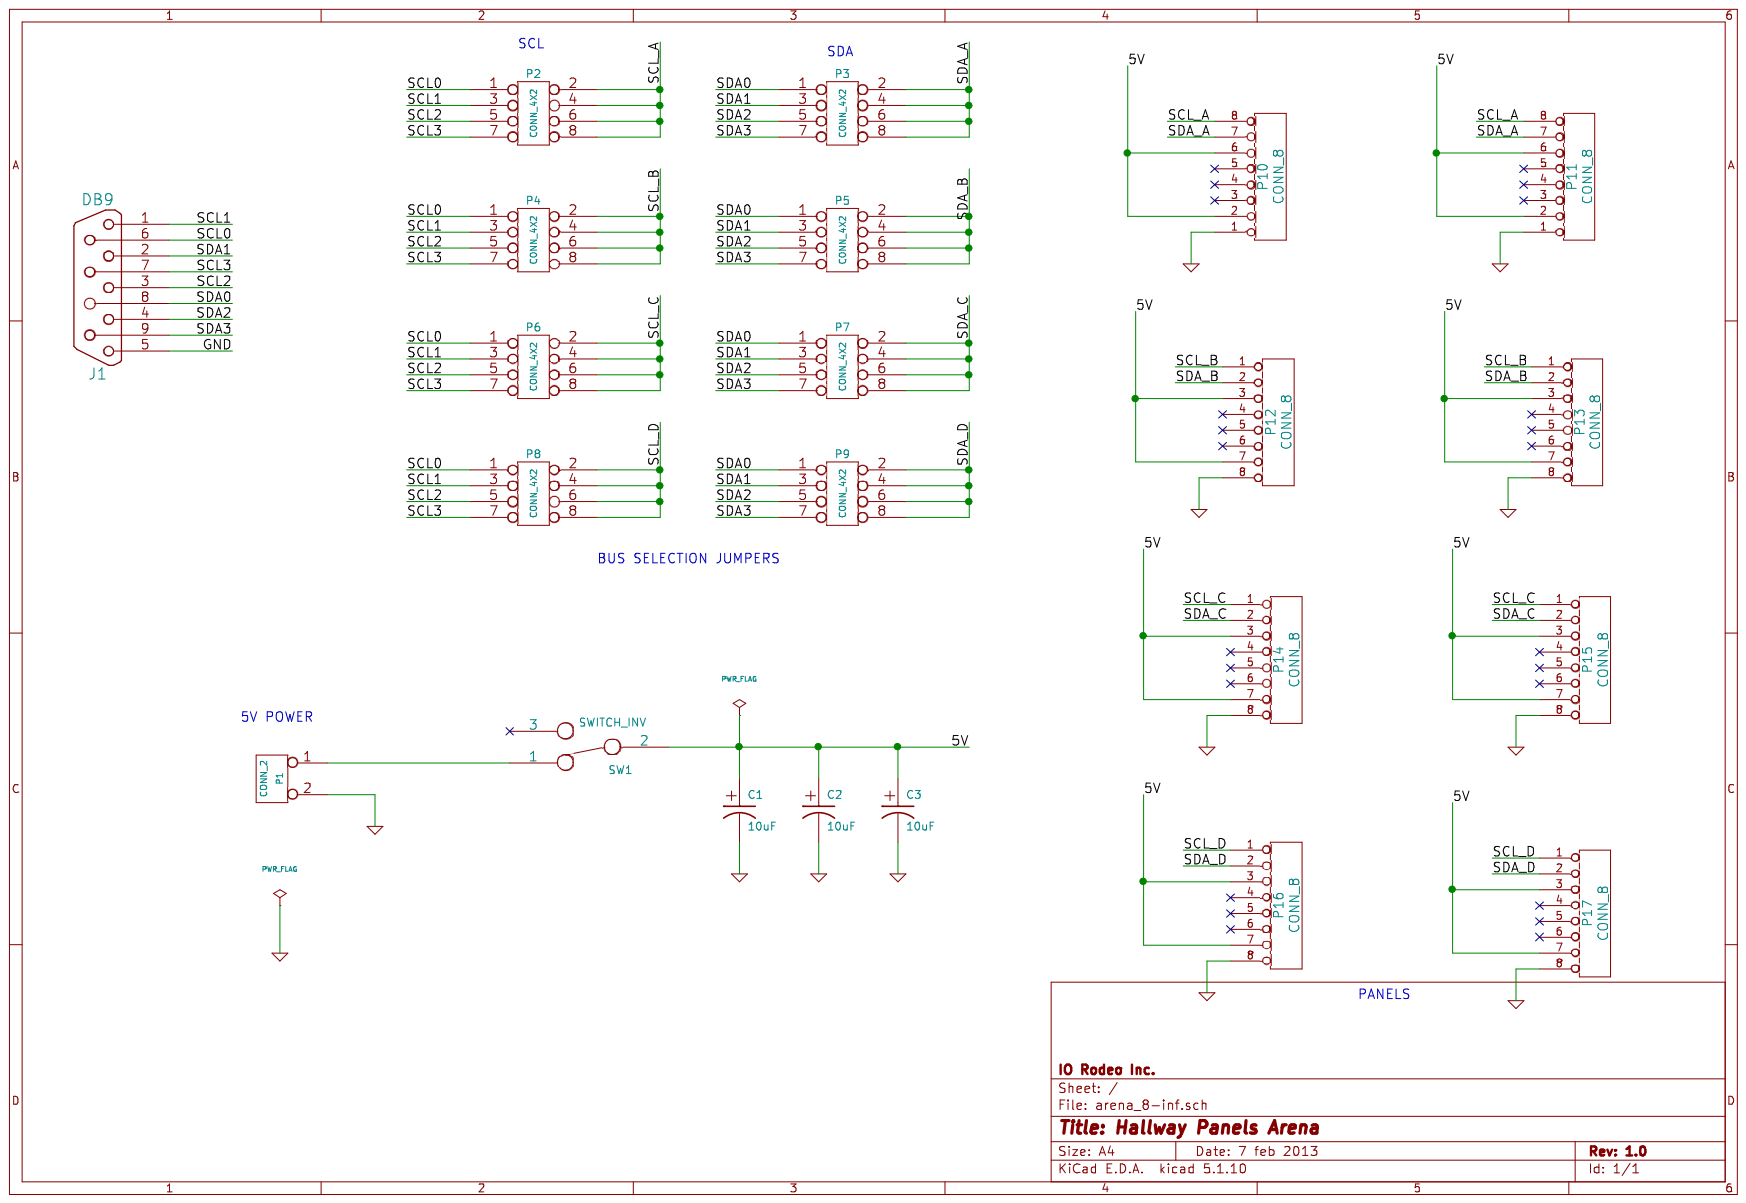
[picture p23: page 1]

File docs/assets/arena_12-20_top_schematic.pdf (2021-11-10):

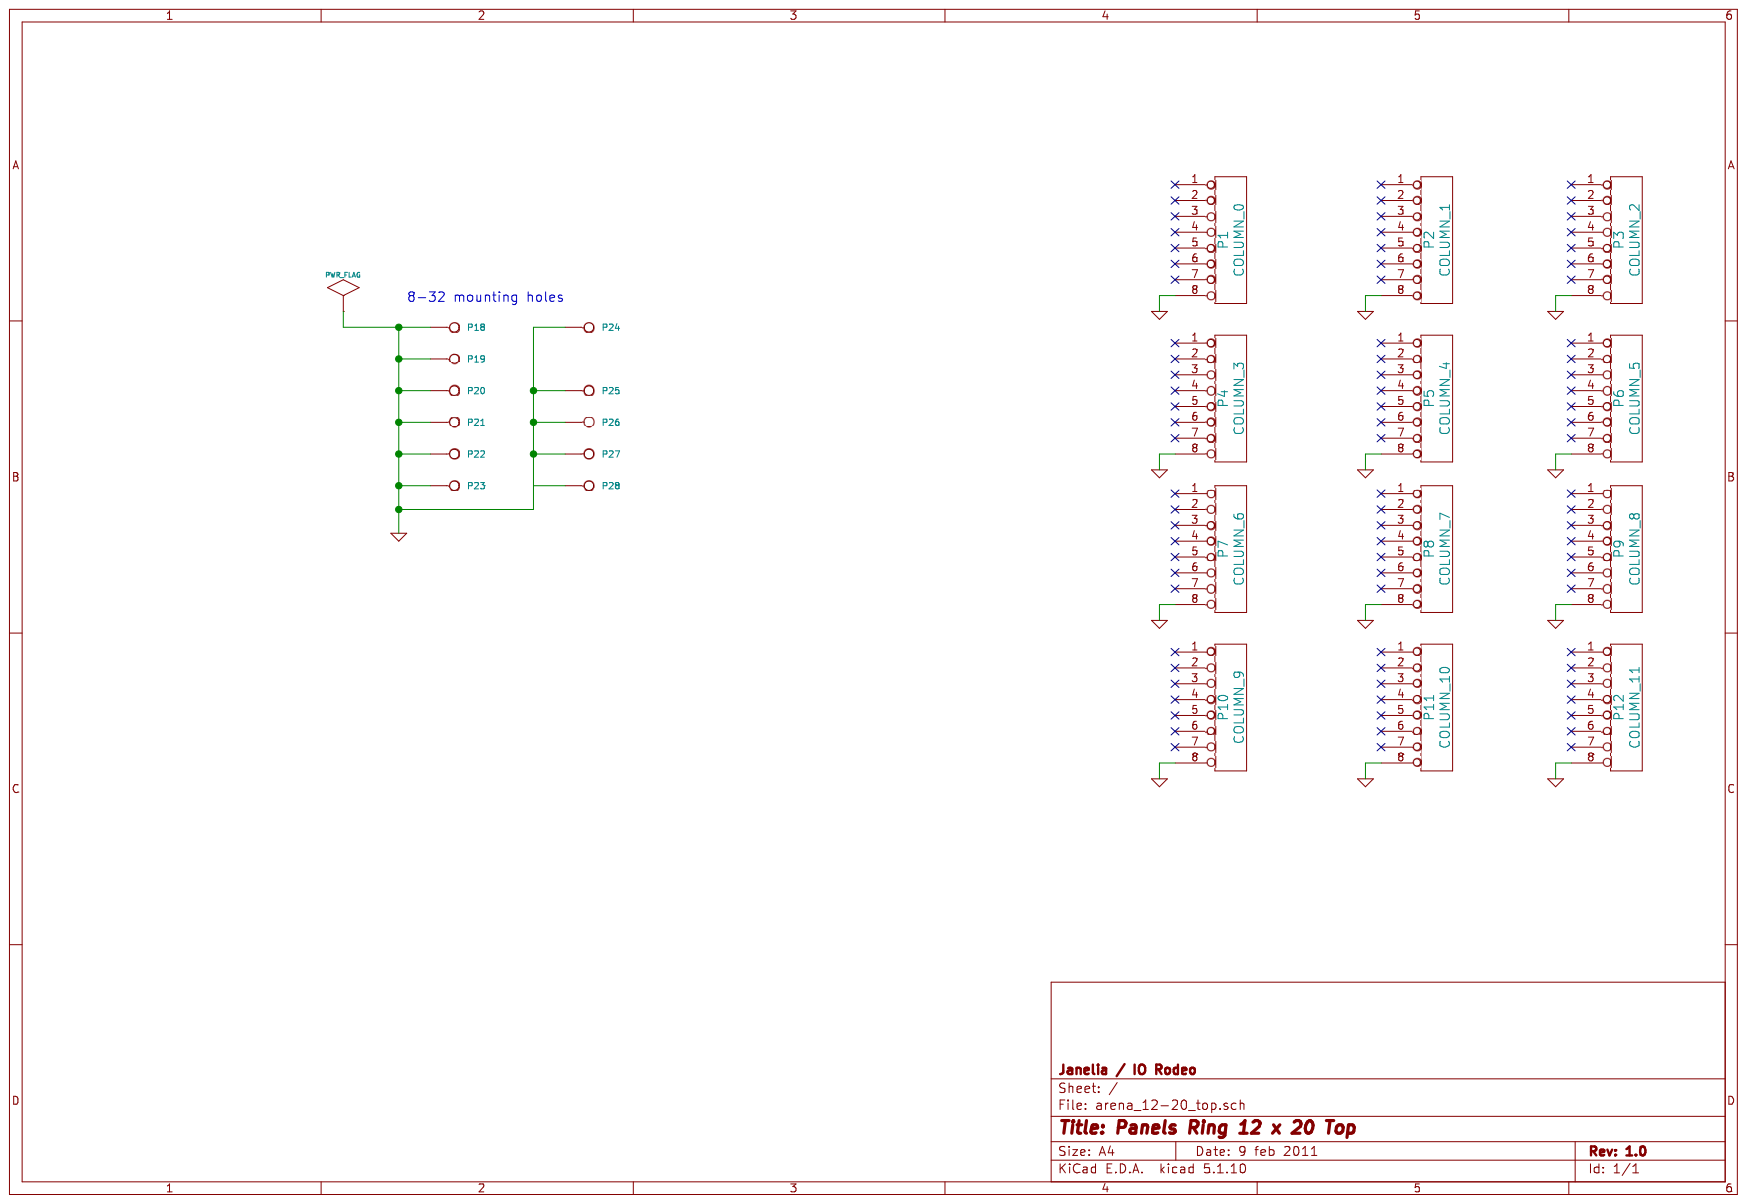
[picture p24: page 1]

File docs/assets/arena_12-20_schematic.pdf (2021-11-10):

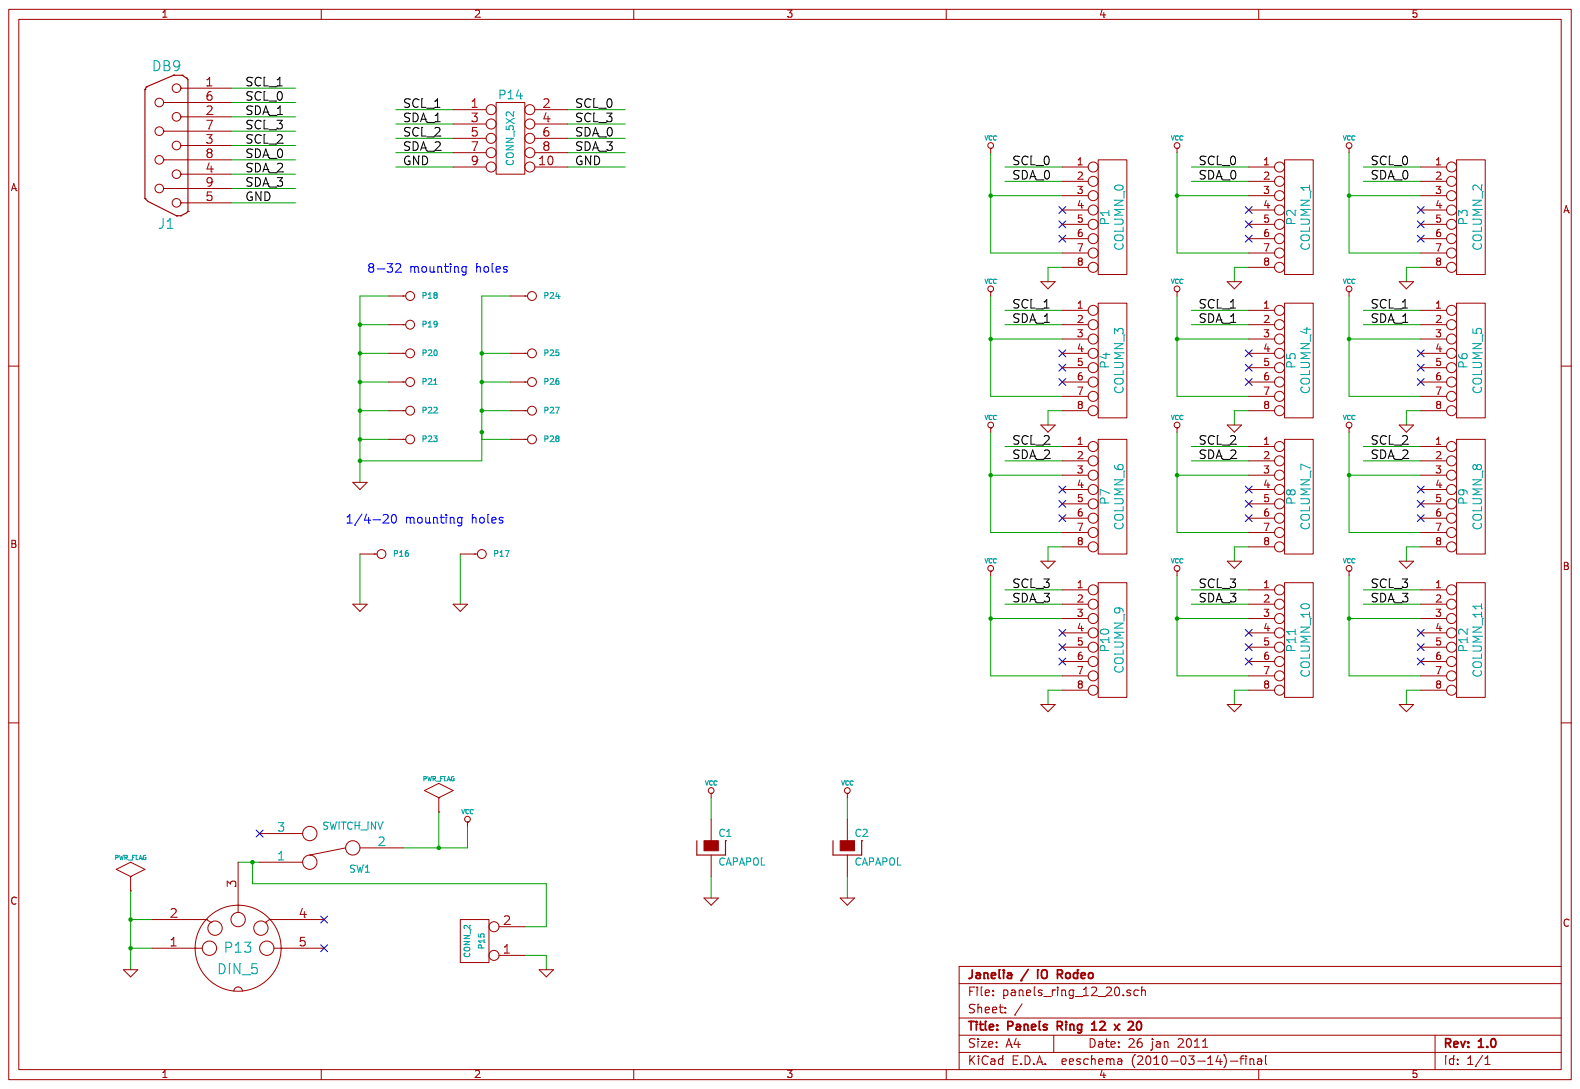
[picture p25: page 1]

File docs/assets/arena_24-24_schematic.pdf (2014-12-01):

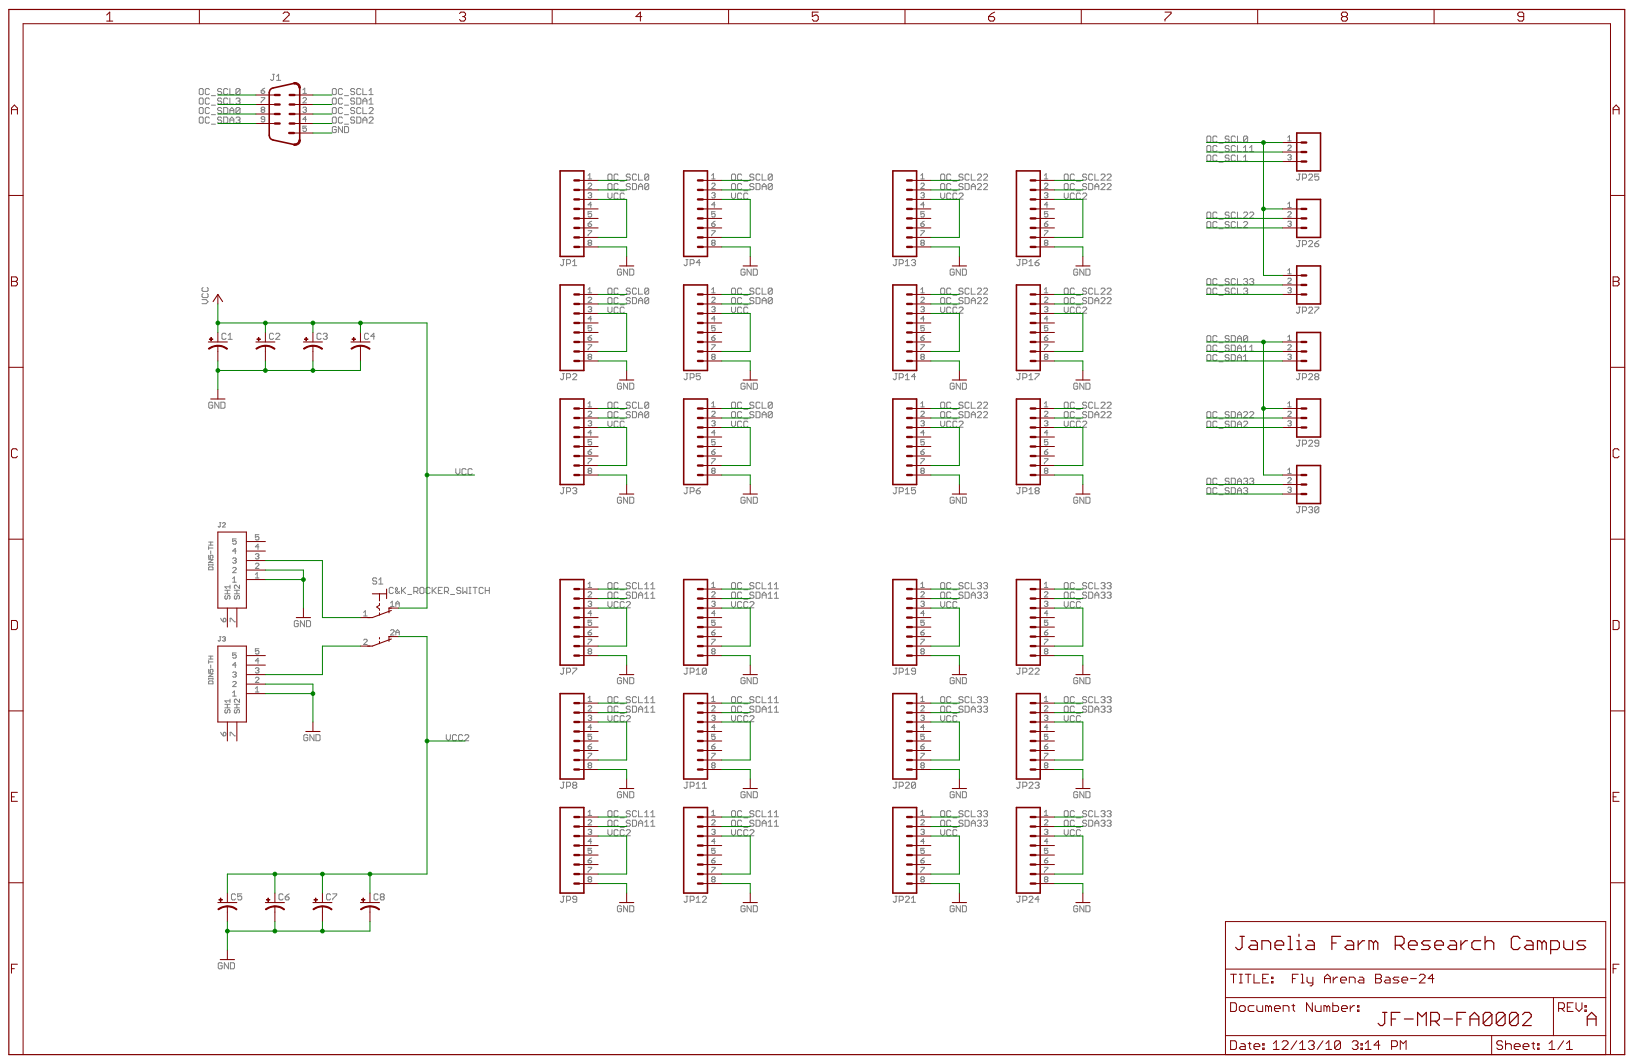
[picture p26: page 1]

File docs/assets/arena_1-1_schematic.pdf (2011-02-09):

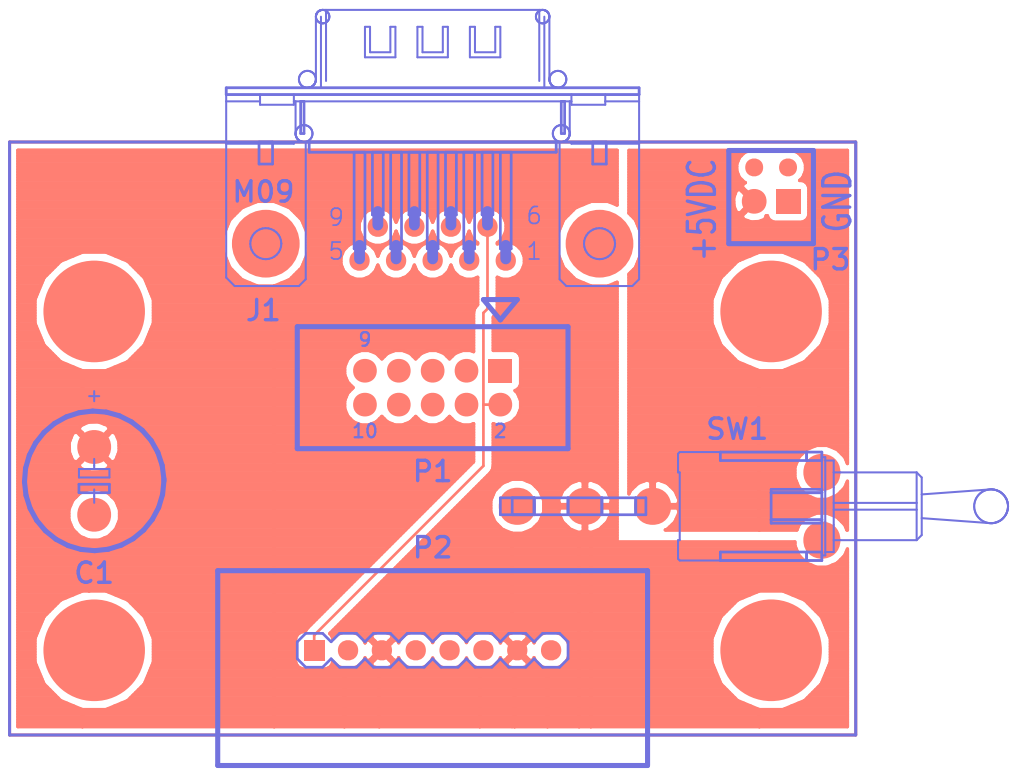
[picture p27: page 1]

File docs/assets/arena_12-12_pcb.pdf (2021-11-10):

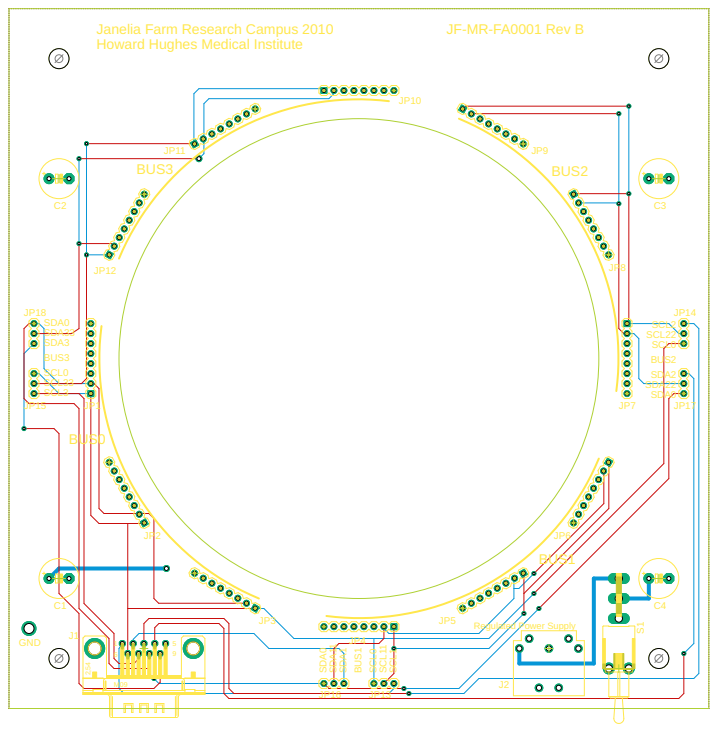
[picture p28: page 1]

Janelia Farm Research Campus 2010
Howard Hughes Medical Institute

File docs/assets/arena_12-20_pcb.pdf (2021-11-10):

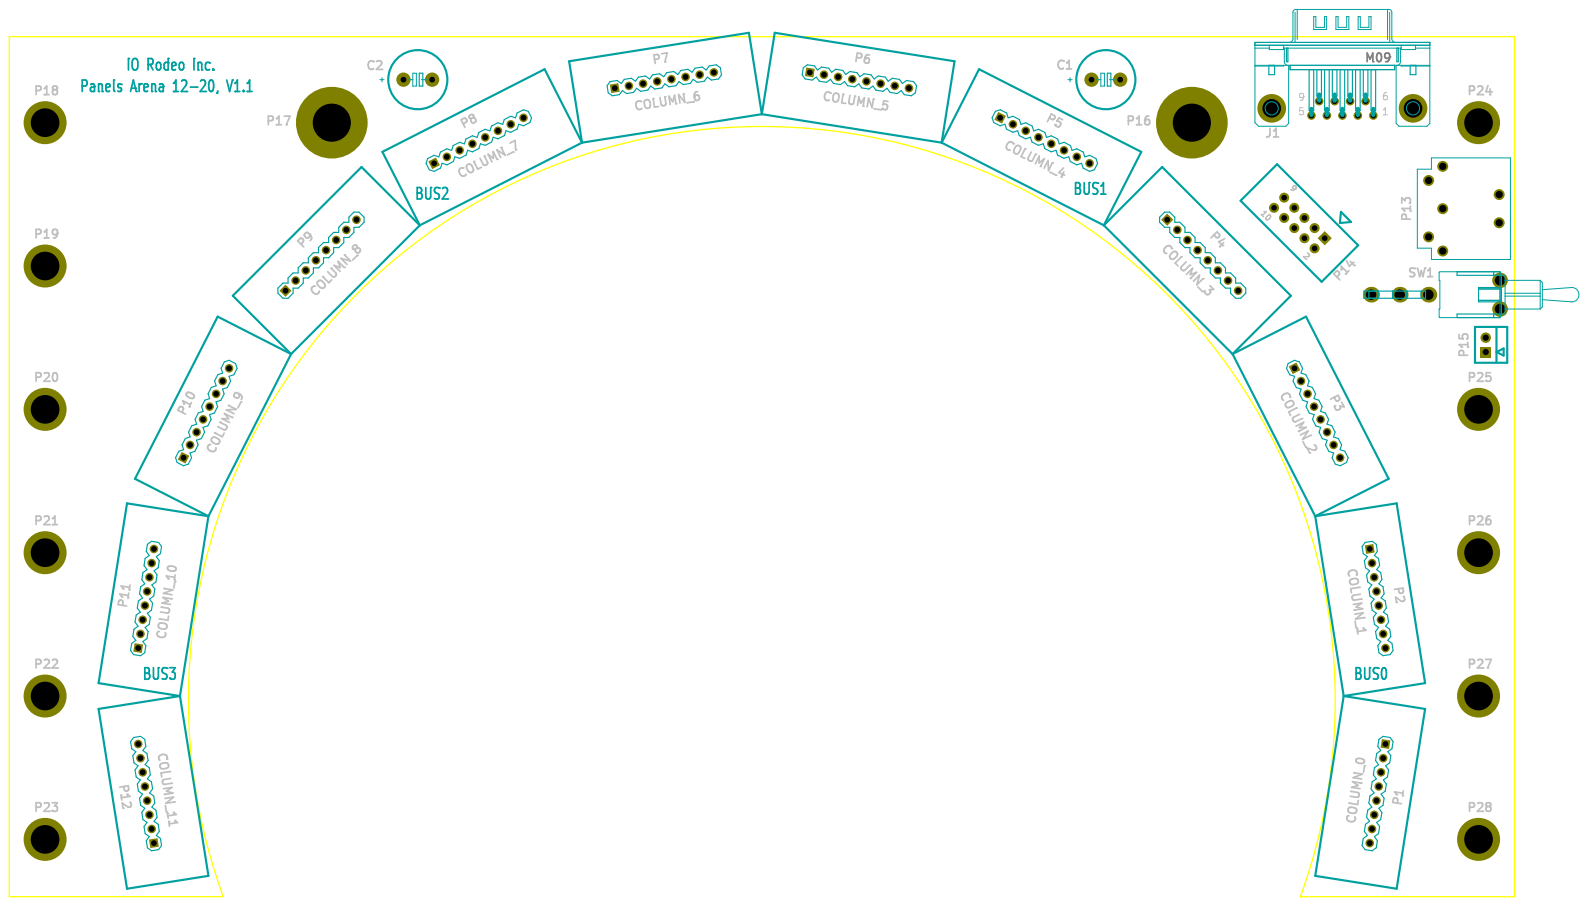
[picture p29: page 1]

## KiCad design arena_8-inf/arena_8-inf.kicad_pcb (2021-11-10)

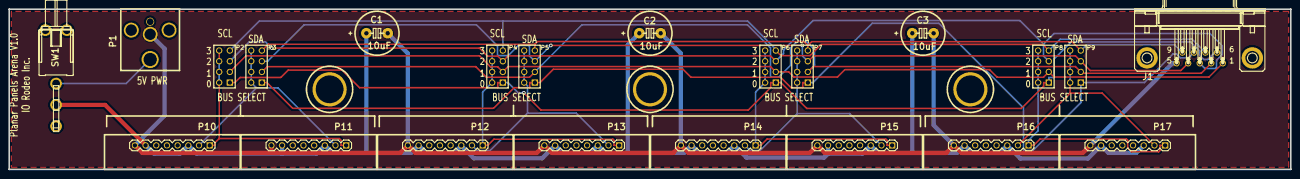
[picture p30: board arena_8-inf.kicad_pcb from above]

Board: 2 copper layers, 304.8 x 38.1 mm, 25 parts (0 on the bottom side), 19 nets.

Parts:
C1, C2, C3: 10uF; JFRC_Capacitor_Polarized
J1: DB9; DB9_M09
M1, M2, M3: 1%2f4-20
P1: CONN_2; DCJACK_2PIN_HIGHCURRENT
P2, P3, P4, P5, P6, P7, P8, P9: CONN_4X2; pin_array_4x2
P10, P11, P12, P13, P14, P15, P16, P17: CONN_8; PANEL_RT_ANG_INV
SW1: SWITCH_INV; JFRC_LPV-1

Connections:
/5V: C1.1, C2.1, C3.1, P10.3, P10.7, P11.3, P11.7, P12.3, P12.7, P13.3, P13.7, P14.3, P14.7, P15.3, P15.7, P16.3, P16.7, P17.3, P17.7, SW1.2
/SCL0: J1.6, P2.1, P4.1, P6.1, P8.1
/SCL1: J1.1, P2.3, P4.3, P6.3, P8.3
/SCL2: J1.3, P2.5, P4.5, P6.5, P8.5
/SCL3: J1.7, P2.7, P4.7, P6.7, P8.7
/SCL_A: P2.2, P2.4, P2.6, P2.8, P10.1, P11.1
/SCL_B: P4.2, P4.4, P4.6, P4.8, P12.1, P13.1
/SCL_C: P6.2, P6.4, P6.6, P6.8, P14.1, P15.1
/SCL_D: P8.2, P8.4, P8.6, P8.8, P16.1, P17.1
/SDA0: J1.8, P3.1, P5.1, P7.1, P9.1
/SDA1: J1.2, P3.3, P5.3, P7.3, P9.3
/SDA2: J1.4, P3.5, P5.5, P7.5, P9.5
/SDA3: J1.9, P3.7, P5.7, P7.7, P9.7
/SDA_A: P3.2, P3.4, P3.6, P3.8, P10.2, P11.2
/SDA_B: P5.2, P5.4, P5.6, P5.8, P12.2, P13.2
/SDA_C: P7.2, P7.4, P7.6, P7.8, P14.2, P15.2
/SDA_D: P9.2, P9.4, P9.6, P9.8, P16.2, P17.2
GND: C1.2, C2.2, C3.2, J1.5, P1.2, P10.8, P11.8, P12.8, P13.8, P14.8, P15.8, P16.8, P17.8
unnamed: P1.1, SW1.1

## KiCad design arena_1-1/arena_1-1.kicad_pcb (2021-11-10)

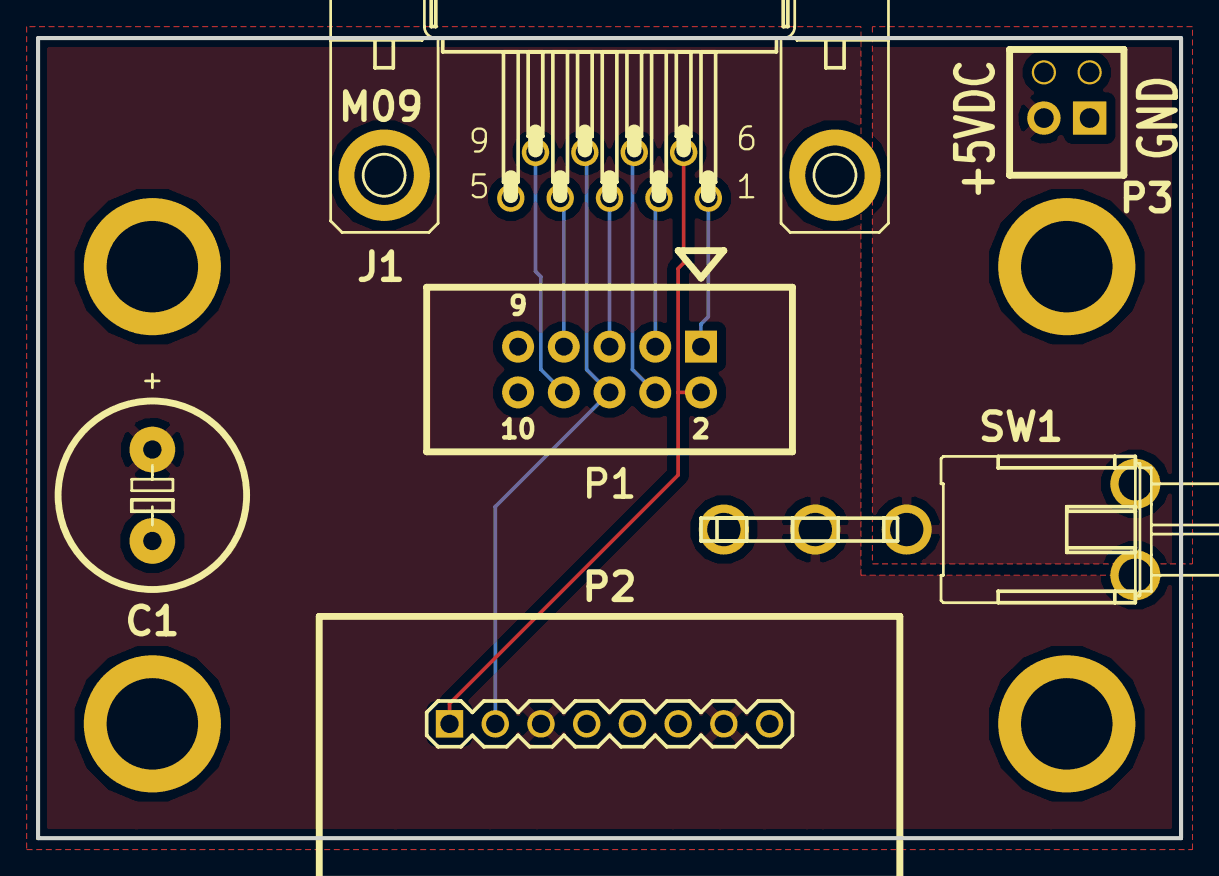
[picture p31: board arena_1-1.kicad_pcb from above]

Board: 2 copper layers, 63.5 x 44.4 mm, 10 parts (0 on the bottom side), 11 nets.

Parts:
C1: CAPAPOL; JFRC_Capacitor_Polarized
J1: DB9; CON-SUBD_M09HP
P1: CONN_5X2; HEADER_5x2_LARGE
P2: COLUMN_0; JFRC_1X08
P3: CONN_2; SCREW_TERMINAL_2
P4, P5, P6, P7: CONN_1; MountingHole
SW1: SWITCH_INV; JFRC_LPV-1

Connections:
/GND: C1.2, J1.5, P1.9, P1.10, P2.8, P3.1, P4.1, P5.1, P6.1, P7.1
/SCL_0: J1.6, P1.2, P2.1
/SCL_1: J1.1, P1.1
/SCL_2: J1.3, P1.5
/SCL_3: J1.7, P1.4
/SDA_0: J1.8, P1.6, P2.2
/SDA_1: J1.2, P1.3
/SDA_2: J1.4, P1.7
/SDA_3: J1.9, P1.8
unnamed: P3.2, SW1.1
VCC: C1.1, P2.3, P2.7, SW1.2

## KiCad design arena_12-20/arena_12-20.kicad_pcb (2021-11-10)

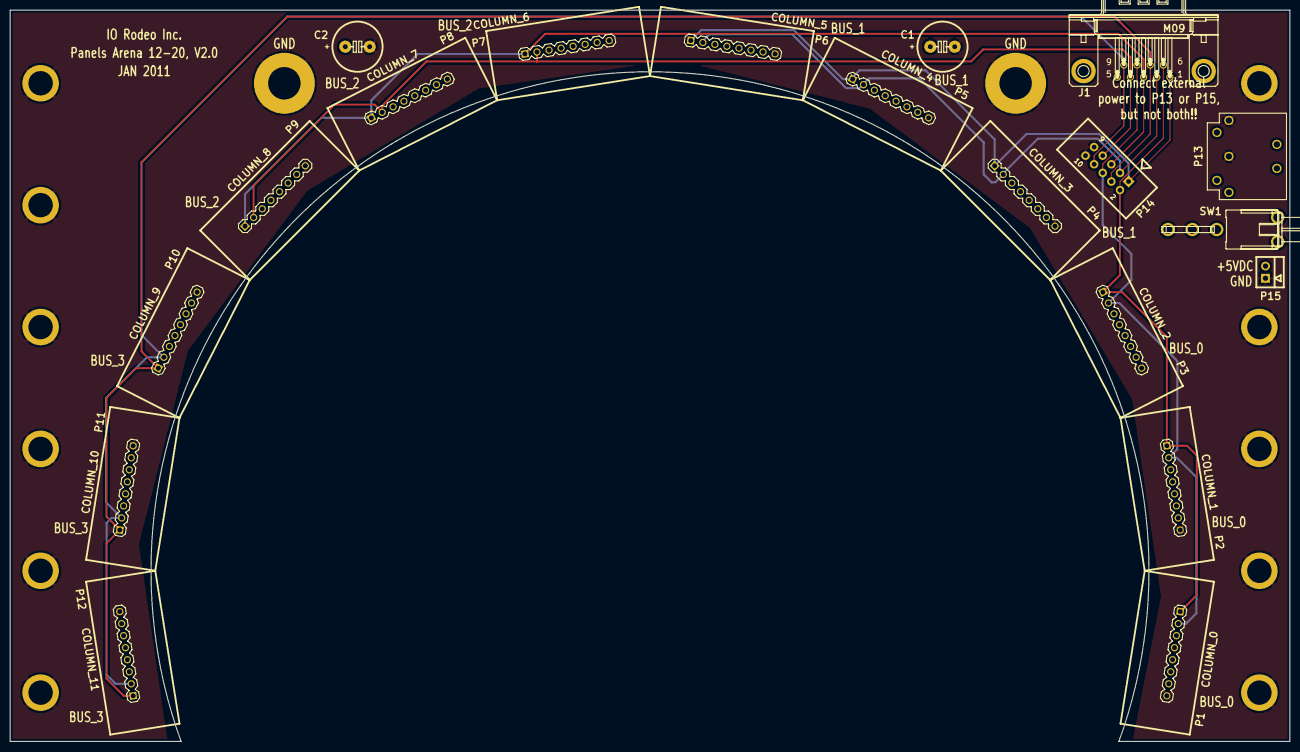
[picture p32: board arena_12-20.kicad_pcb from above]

Board: 4 copper layers, 266.7 x 152.4 mm, 32 parts (0 on the bottom side), 11 nets.

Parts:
C1, C2: CAPAPOL; JFRC_Capacitor_Polarized
J1: DB9; CON-SUBD_M09HP
P1: COLUMN_0; JFRC_1X08
P2: COLUMN_1; JFRC_1X08
P3: COLUMN_2; JFRC_1X08
P4: COLUMN_3; JFRC_1X08
P5: COLUMN_4; JFRC_1X08
P6: COLUMN_5; JFRC_1X08
P7: COLUMN_6; JFRC_1X08
P8: COLUMN_7; JFRC_1X08
P9: COLUMN_8; JFRC_1X08
P10: COLUMN_9; JFRC_1X08
P11: COLUMN_10; JFRC_1X08
P12: COLUMN_11; JFRC_1X08
P13: DIN_5; JFRC_DIN5-TH
P14: CONN_5X2; HEADER_5x2_LARGE
P15: CONN_2; Header_Shrouded_2_Pin
P16, P17: CONN_1; GroundMount
P18, P19, P20, P21, P22, P23, P24, P25, P26, P27, P28: CONN_1; MountingHole
SW1: SWITCH_INV; JFRC_LPV-1

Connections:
/SCL_0: J1.6, P1.1, P2.1, P3.1, P14.2
/SCL_1: J1.1, P4.1, P5.1, P6.1, P14.1
/SCL_2: J1.3, P7.1, P8.1, P9.1, P14.5
/SCL_3: J1.7, P10.1, P11.1, P12.1, P14.4
/SDA_0: J1.8, P1.2, P2.2, P3.2, P14.6
/SDA_1: J1.2, P4.2, P5.2, P6.2, P14.3
/SDA_2: J1.4, P7.2, P8.2, P9.2, P14.7
/SDA_3: J1.9, P10.2, P11.2, P12.2, P14.8
GND: C1.2, C2.2, J1.5, P1.8, P2.8, P3.8, P4.8, P5.8, P6.8, P7.8, P8.8, P9.8, P10.8, P11.8, P12.8, P13.1, P13.2, P14.9, P14.10, P15.1, P16.1, P17.1, P18.1, P19.1, P20.1, P21.1, P22.1, P23.1, P24.1, P25.1, P26.1, P27.1, P28.1
unnamed: P13.3, P15.2, SW1.1
VCC: C1.1, C2.1, P1.3, P1.7, P2.3, P2.7, P3.3, P3.7, P4.3, P4.7, P5.3, P5.7, P6.3, P6.7, P7.3, P7.7, P8.3, P8.7, P9.3, P9.7, P10.3, P10.7, P11.3, P11.7, P12.3, P12.7, SW1.2

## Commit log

2010-12-28 Project creation.
    [$savepcb.brd, panels_ring_12_20.brd, panels_ring_12_20.drl, panels_ring_12_20.sch]
2010-12-28 Modified board to put DIN5 connector on the left as per Gaby's suggestion.
    [$savepcb.brd, panels_ring_12_20.brd, panels_ring_12_20.sch]
2010-12-28 Re-routed board so that the db9, din5, switch and jumper are all on the left hand side of the board.
    [$savepcb.brd, panels_ring_12_20.brd, panels_ring_12_20.sch]
2010-12-29 Shortened the board a bit on Gaby's suggestion. Fixed some of the footprint modules so that the pads have solder mask etc.
    [$savepcb.brd, panels_ring_12_20.brd, panels_ring_12_20.drl, panels_ring_12_20.sch]
2010-12-29 Created gerber and drill files for version 1.0 of the boards.
    [$savepcb.brd, panels_ring_12_20.drl]
2010-12-29 Add top plate design for 12-20 arenas.
    [panels_ring_12_20.brd, panels_ring_12_20_top.brd, panels_ring_12_20_top.sch]
2010-12-29 Swapped the power connector and power switch.
    [panels_ring_12_20.brd]
2010-12-29 Remade gerber files - to incorporate the latest changes.
    [panels_ring_12_20.brd, panels_ring_12_20.drl]
2011-02-07 Version 2 redesign. Increased arena radius so panels will fit.
    [$savepcb.brd, panels_ring_12_20-Back.gbl, panels_ring_12_20-Front.gtl, panels_ring_12_20-Inner_L1.gbr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]
2011-02-07 Added arena_mini. Moved .mod file.
    [panels_arena_mini.brd, panels_arena_mini.sch, panels_ring_12_20.brd]
2011-02-08 Modified arena_mini board
    [$savepcb.brd, panels_arena_mini-Front.gtl, panels_arena_mini-SilkS_Front.gto]
2011-02-09 Finished Ver. 1 board design
    [$savepcb.brd, panels_arena_mini-Back.gbl, panels_arena_mini-Front.gtl, panels_arena_mini-Mask_Back.gbs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]
2011-02-09 Finished Ver. 1 of panels_ring_12_20_top
    [panels_ring_12_20_top-Back.gbl, panels_ring_12_20_top-Front.gtl, panels_ring_12_20_top-Mask_Back.gbs, panels_ring_12_20_top-Mask_Front.gts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]
2013-02-11 Added planar arena design.
    [$savepcb.brd, planar_arena.brd, planar_arena.dsn, planar_arena.sch]
2013-02-13 Added gerber files for planar arenas.
    [planar_arena-Back.gbl, planar_arena-Front.gtl, planar_arena-Mask_Back.gbs, planar_arena-Mask_Front.gts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]
2013-02-13 Added design of planar arena base plate.
    [$savepcb.brd]
2013-02-28 Remade planar arena gerbers.
    [planar_arena-Back.gbl, planar_arena-Front.gtl, planar_arena-Mask_Back.gbs, planar_arena-Mask_Front.gts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]
2013-08-07 Modified planar arena base.
    [planar_arena_8x_base.dxf]
2013-08-21 Added lower and upper support plates to planar arena base plate.
    [base.dxf, lower.dxf, upper.dxf]
2014-03-11 Added .drl file to version 2.0 of 12_20 ring gerber files.
    [panels_ring_12_20.drl]
2014-12-01 Added full arena designs.
    [Fly Arena Base-24.GBL, Fly Arena Base-24.GBS, Fly Arena Base-24.GTL, Fly Arena Base-24.GTO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]
2014-12-01 Renamed 12-ring eagle file sub-directory.
    [arena-B.brd, arena-B.sch]
2021-11-10 KiCAD cleanup
    [panels_ring_12_20.brd, panels_ring_12_20.drl, panels_ring_12_20.dsn, panels_ring_12_20.kicad_pcb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]
2021-11-10 more cleanup
    [panels_ring_12_20.sch]
2021-11-10 start documentation of arena
    [arena_12-20-Back.gbl, arena_12-20-Front.gtl, arena_12-20-Inner_L1.gbr, arena_12-20-Inner_L2.gbr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]
2021-11-10 consistent file renaming
    [arena_12-20-Back.gbl, arena_12-20-Front.gtl, arena_12-20-Inner_L1.gbr, arena_12-20-Inner_L2.gbr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]
2021-11-10 cleanup arena 12-20 top
    [arena_12-20_top-Back.gbl, arena_12-20_top-Front.gtl, arena_12-20_top-Mask_Back.gbs, arena_12-20_top-Mask_Front.gts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]
2021-11-10 rename arena_12-20; optimize images
    [arena_12-20_top-Back.gbl, arena_12-20_top-Front.gtl, arena_12-20_top-Mask_Back.gbs, arena_12-20_top-Mask_Front.gts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]
2021-11-10 cleanup arena 1-1
    [$savepcb.brd, arena_1-1-Back.gbl, arena_1-1-Front.gtl, arena_1-1-Mask_Back.gbs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]
2021-11-10 cleanup arena_8-inf
    [$savepcb.brd, arena_8-inf-Back.gbl, arena_8-inf-Front.gtl, arena_8-inf-Mask_Back.gbs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]
2021-11-10 rename project folder
    [arena_8-inf-Back.gbl, arena_8-inf-Front.gtl, arena_8-inf-Mask_Back.gbs, arena_8-inf-Mask_Front.gts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]
2021-11-10 add enclosure
    [base.dxf, lower.dxf, planar_arena_8x_base.dxf, upper.dxf]
2021-11-10 fix file naming
    [arena-B.GBL, arena-B.GBS, arena-B.GTL, arena-B.GTO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]
2021-11-10 integrate 24-24 arena
    [Fly Arena Base-24.GBL, Fly Arena Base-24.GBS, Fly Arena Base-24.GTL, Fly Arena Base-24.GTO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]
